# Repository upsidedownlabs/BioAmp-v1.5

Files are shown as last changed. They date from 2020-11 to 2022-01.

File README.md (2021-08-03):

# BioAmp v1.5

                       

BioAmp v1.5 is a single chip Bio-potential amplifier for recording any Bio-potential signal non-invasively. It's compatible with [Backyard Brains Spike Recorder](https://backyardbrains.com/products/spikerecorder), which you can use to record and visualize all the Bio-potential signals. 

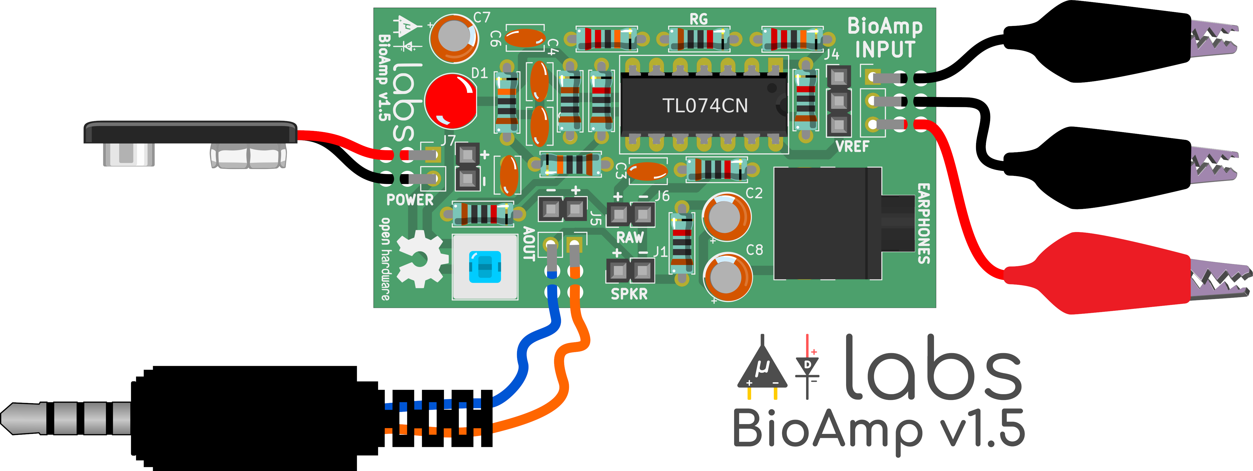
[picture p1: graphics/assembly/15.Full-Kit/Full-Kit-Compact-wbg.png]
Upside Down Labs BioAmp v1.5.6 back (https://bit.ly/BioAmp-v1_5)


## Hardware

BioAmp v1.5 has been created using [KiCad](https://www.kicad.org/) and all the design files can be found under [hardware](hardware/) folder, including production [Gerber](hardware/gerbers) files. Images below shows a quick overview of the hardware design.

| Front             |  Back |
| :-------------------------: | :-------------------------: |
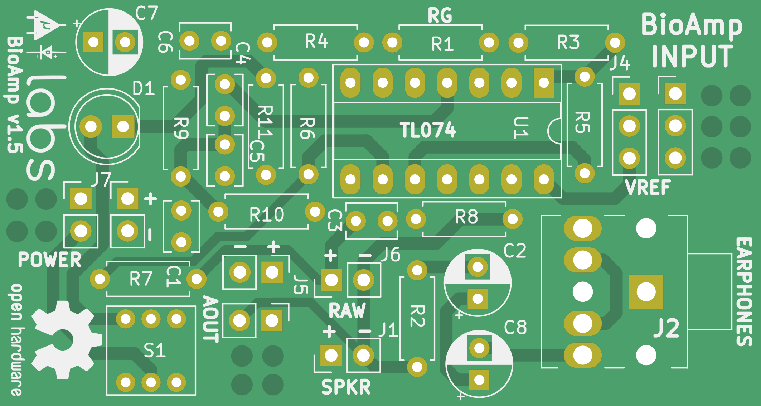
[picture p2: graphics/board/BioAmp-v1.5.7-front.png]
Upside Down Labs BioAmp v1.5.6 front
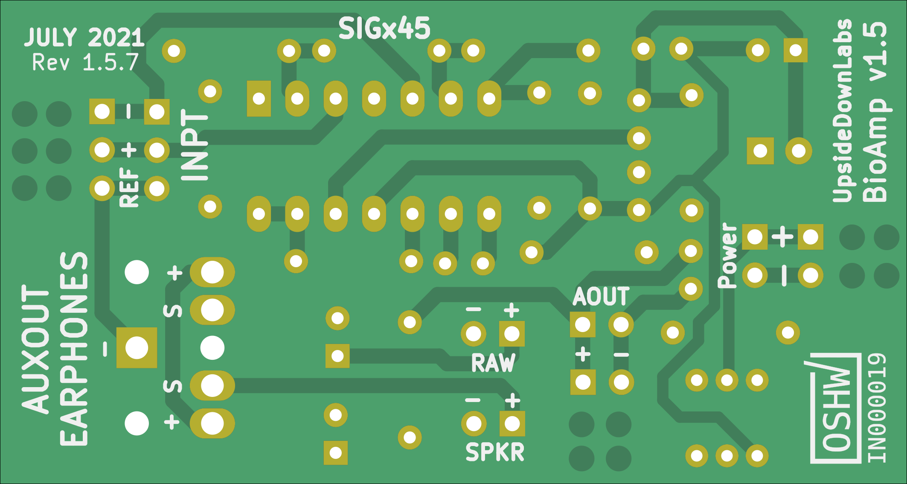
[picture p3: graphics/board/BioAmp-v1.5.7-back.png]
Upside Down Labs BioAmp v1.5.6 back
|   |  |

|Assembled PCB|
|:--:|
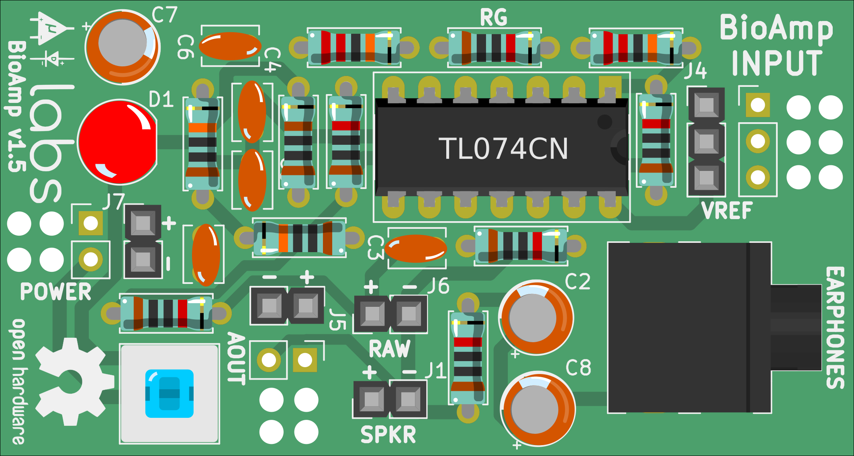
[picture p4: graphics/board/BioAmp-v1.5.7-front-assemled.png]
Upside Down Labs BioAmp v1.5.6 front
||

| Dimensions             |  Schematic  |
| :-------------------------: | :-------------------------: |
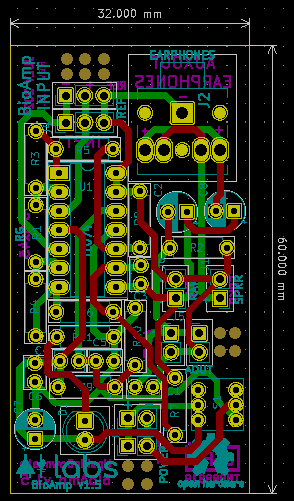
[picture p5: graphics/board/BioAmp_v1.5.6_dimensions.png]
Upside Down Labs BioAmp v1.5.6 dimensions
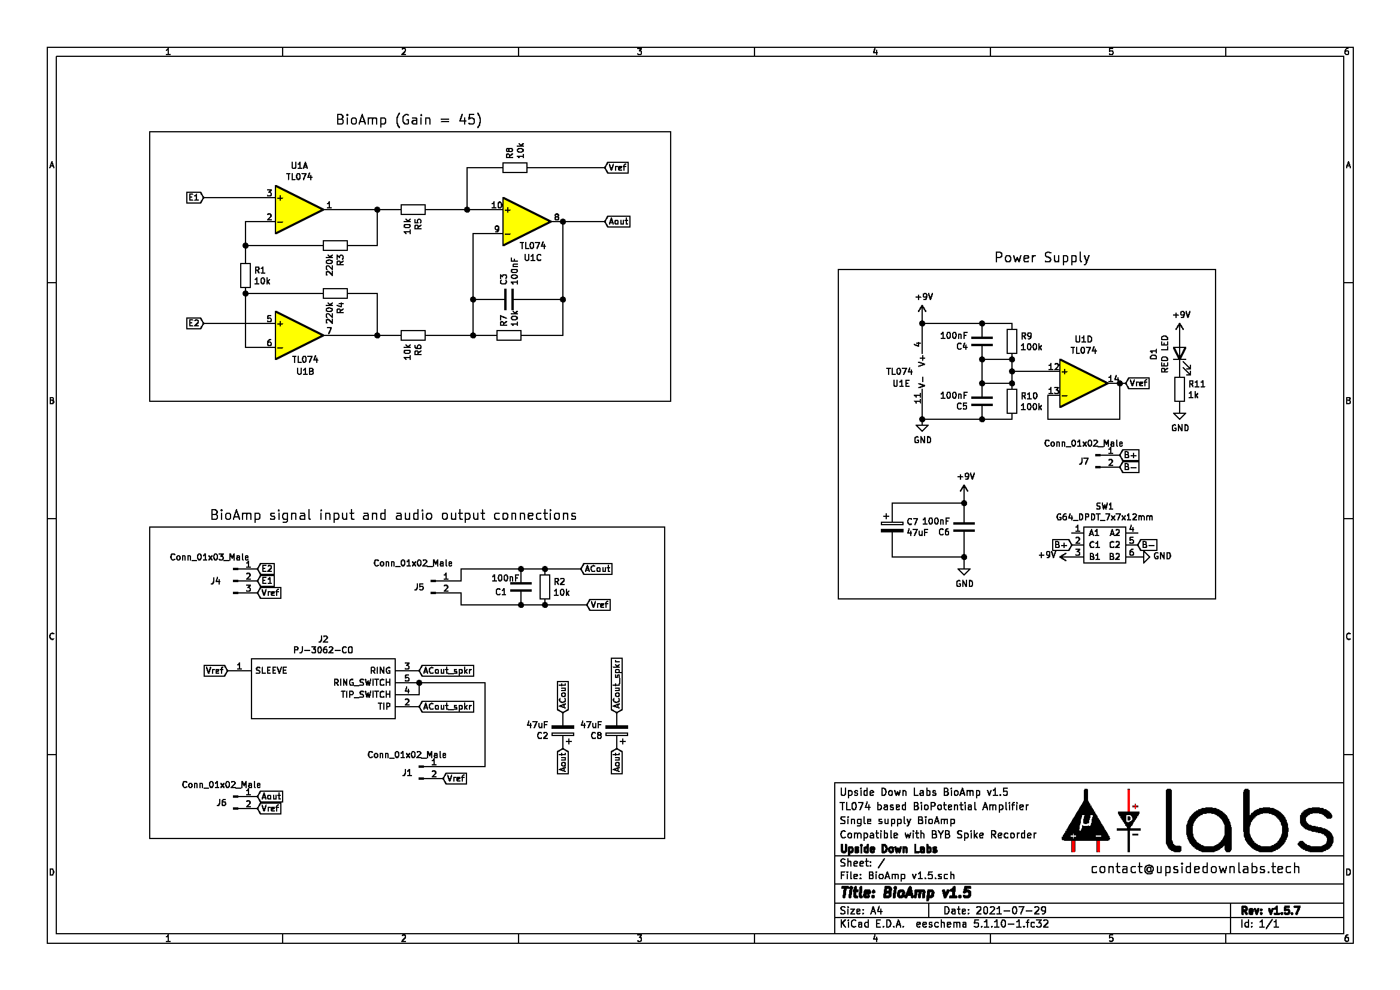
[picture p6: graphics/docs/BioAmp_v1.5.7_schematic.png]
Upside Down Labs BioAmp v1.5.6 schematic
| 32x60mm  |  |

| Licenses Facts              |  OSHWA Certification |
| :-------------------------: | :-------------------------: |
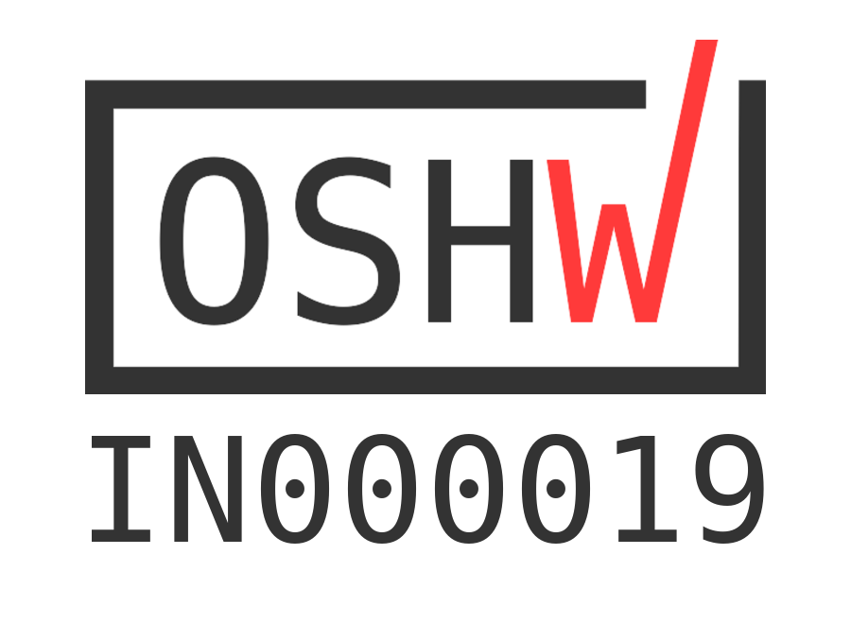
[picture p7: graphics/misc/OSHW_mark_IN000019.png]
Open Source Hardware Certification mark
| <a href="LICENSE.md">Open Source Licenses Facts</a>  |  |

## License
#### Hardware
CERN Open Hardware License Version 2 - Strongly Reciprocal ([CERN-OHL-S-2.0](https://spdx.org/licenses/CERN-OHL-S-2.0.html)).

#### Software
MIT open source [license](http://opensource.org/licenses/MIT).

#### Documentation:
<br />This work is licensed under a <a rel="license" href="http://creativecommons.org/licenses/by/4.0/">Creative Commons Attribution 4.0 International License</a>.

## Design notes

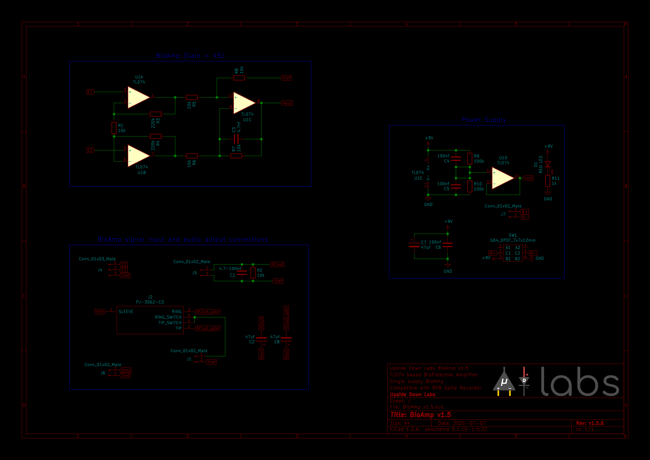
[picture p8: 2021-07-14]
graphics/docs/BioAmp_v1.5.6_schematic_hc.png

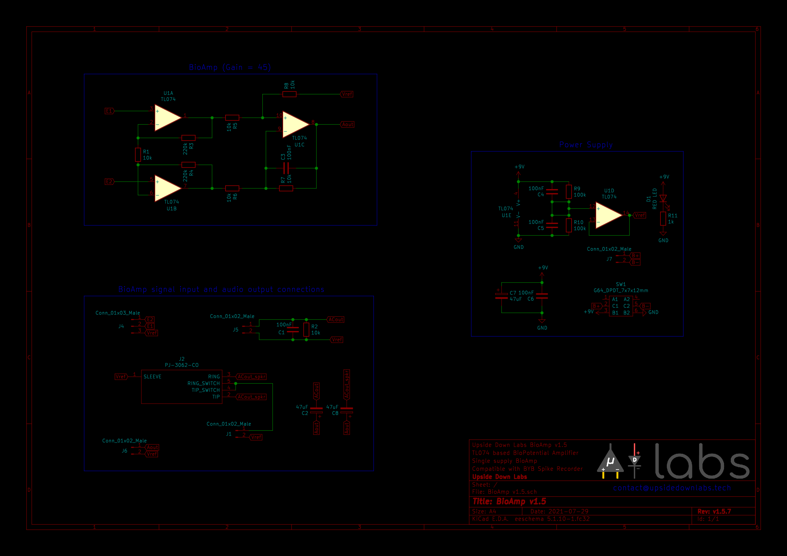
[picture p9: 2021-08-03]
graphics/docs/BioAmp_v1.5.7_schematic_hc.png

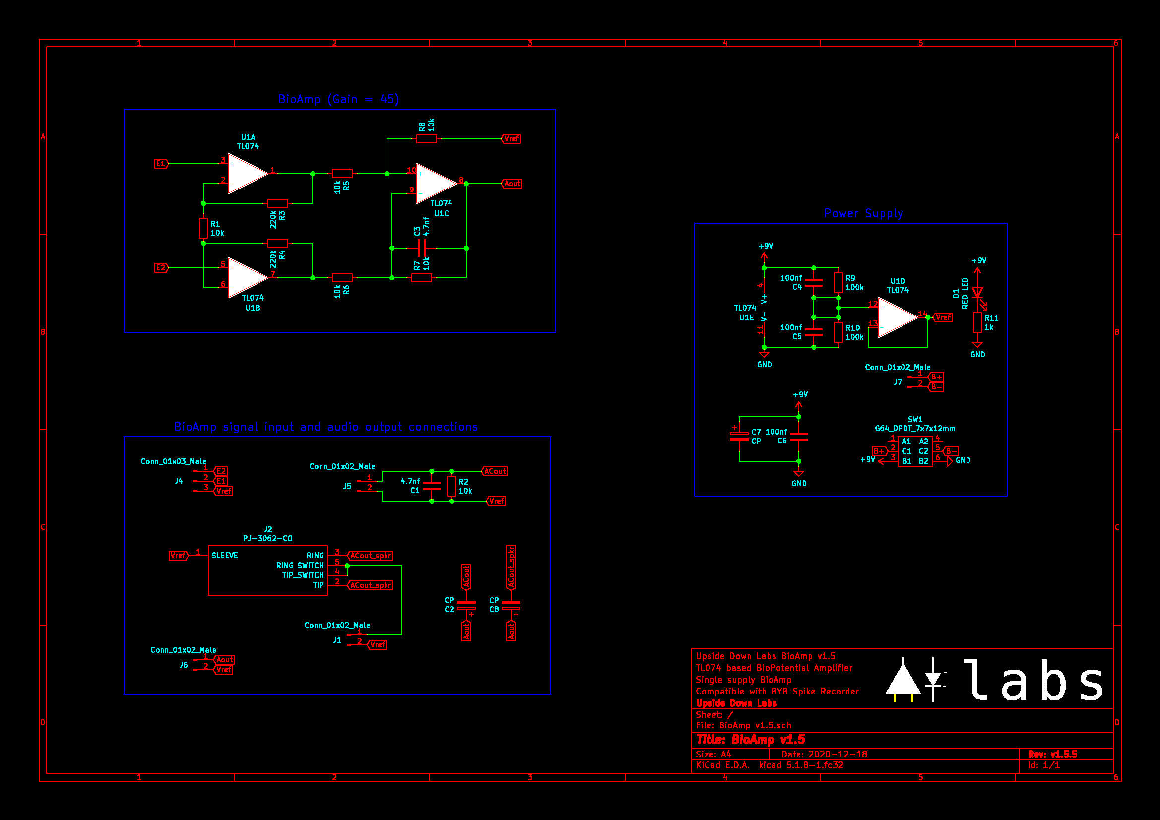
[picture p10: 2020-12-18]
graphics/docs/BioAmp_v1.5.5_schematic_hc.png

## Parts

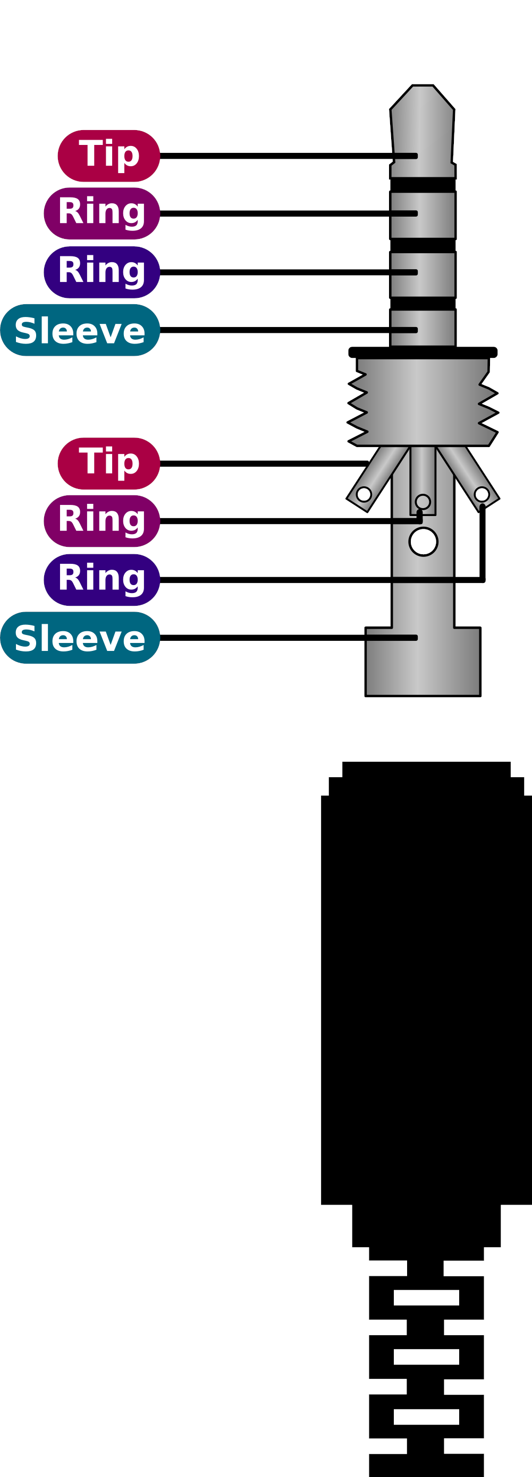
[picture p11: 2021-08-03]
graphics/assembly/Parts/3.5mm-Male/3.5mm-Male-wbg.png

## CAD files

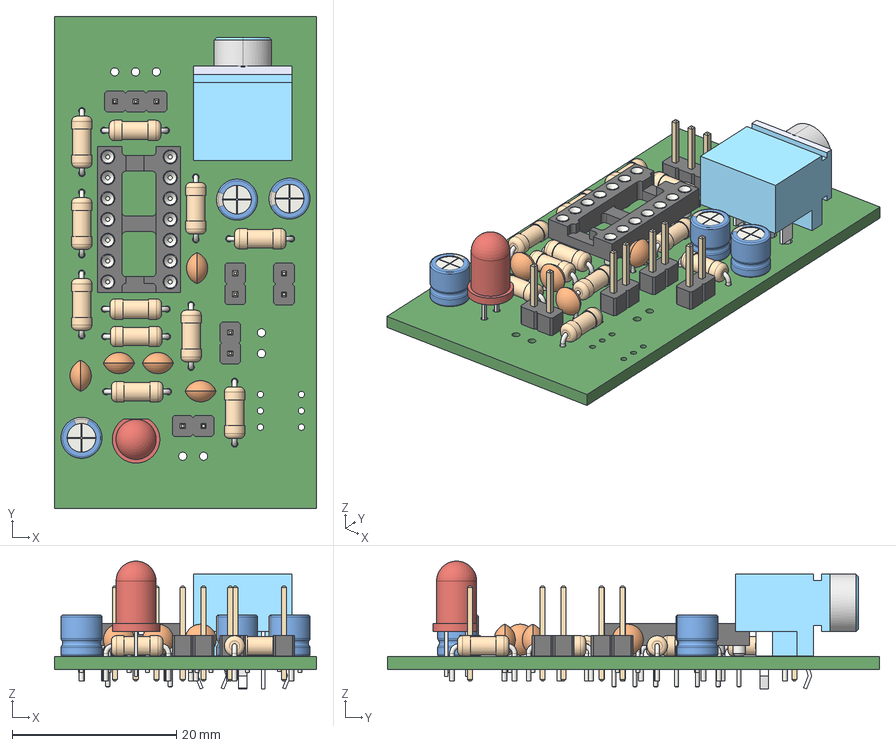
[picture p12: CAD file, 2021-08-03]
graphics/3D/BioAmp v1.5.step
32.0 x 60.0 x 15.6 mm

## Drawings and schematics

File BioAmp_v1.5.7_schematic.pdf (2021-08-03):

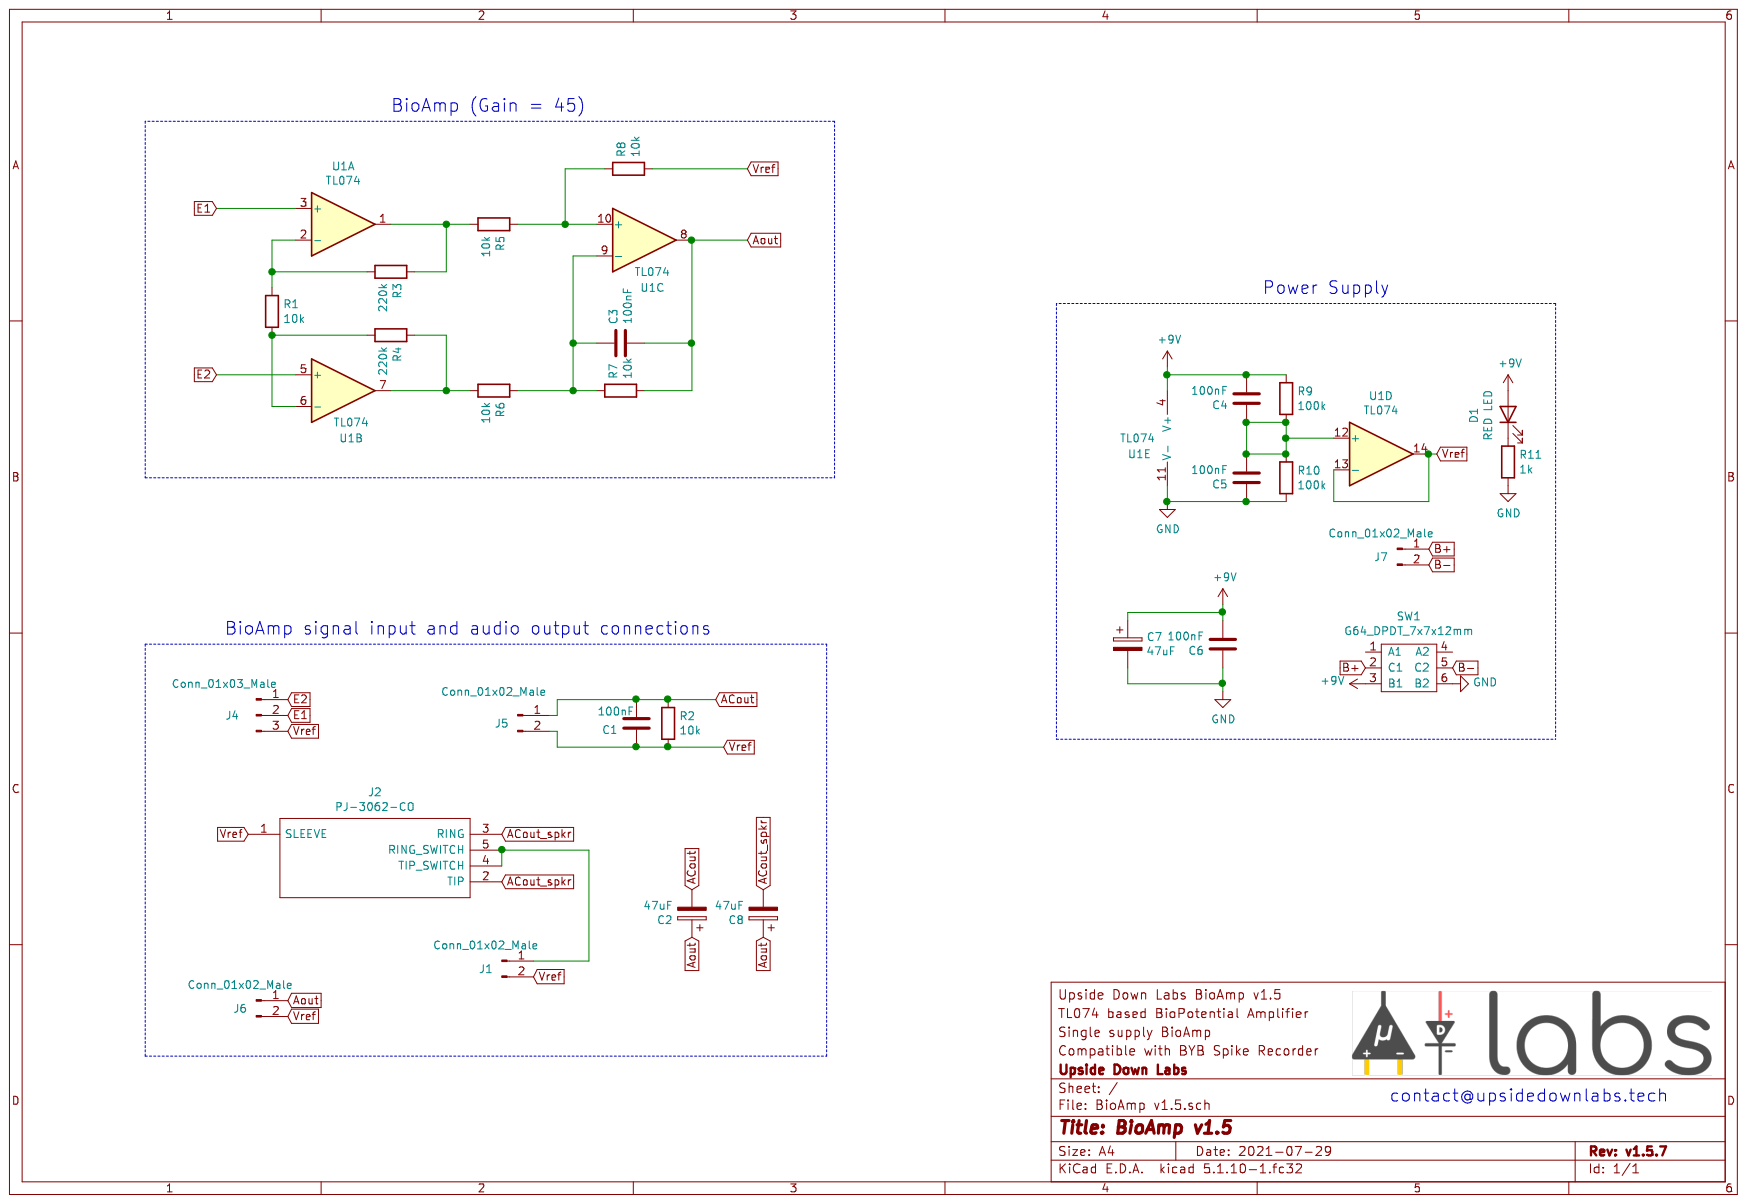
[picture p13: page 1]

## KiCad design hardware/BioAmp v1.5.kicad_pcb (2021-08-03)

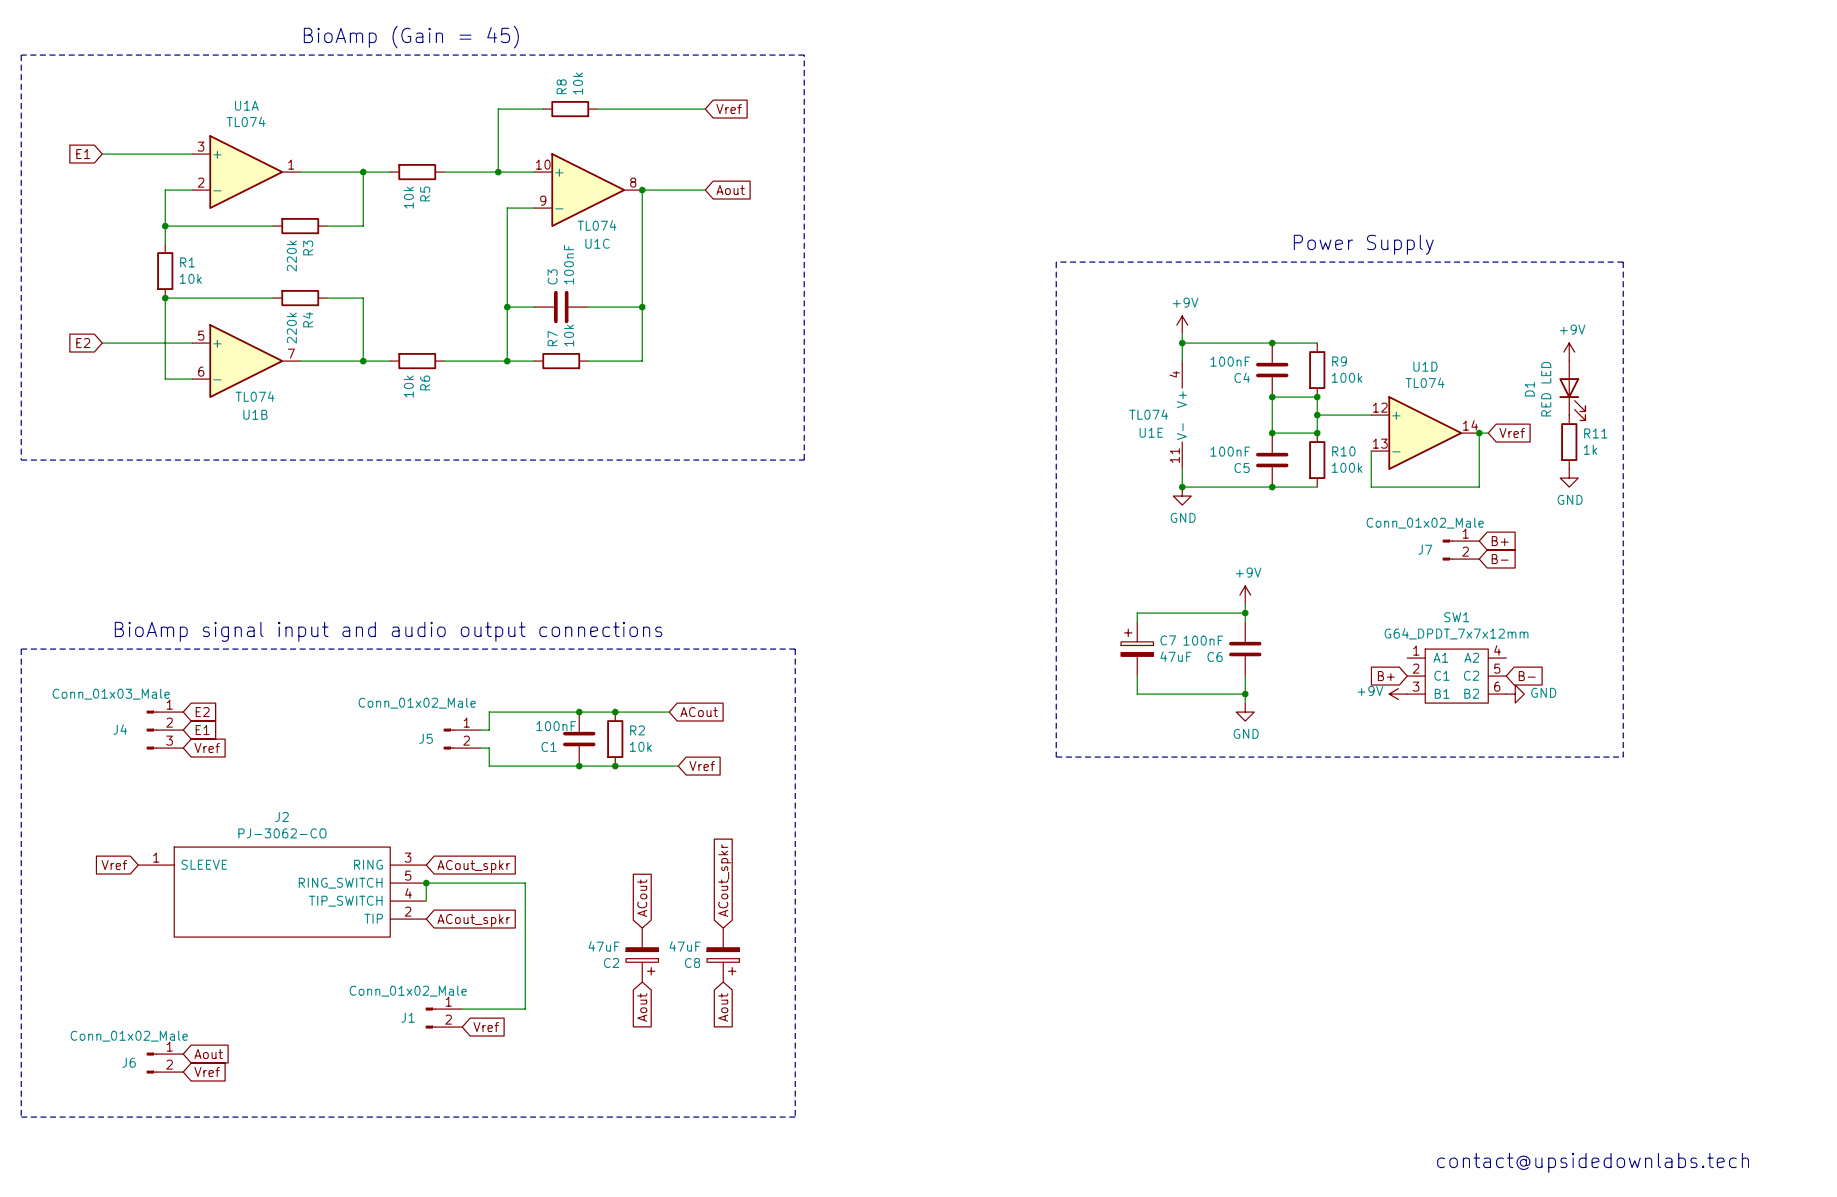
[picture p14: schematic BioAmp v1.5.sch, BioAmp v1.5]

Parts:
C1, C3, C4, C5, C6: 100nF; C_Disc_D3.8mm_W2.6mm_P2.50mm
C2, C7, C8: 47uF; CP_Radial_D5.0mm_P2.50mm
D1: RED LED; LED_D5.0mm
J1, J5, J6, J7: Conn_01x02_Male; PinHeader_1x02_P2.54mm_Vertical
J2: PJ-3062-CO; PJ3062CO; Manufacturer_Part_Number PJ-3062-CO
J4: Conn_01x03_Male; PinHeader_1x03_P2.54mm_Vertical
R1, R2, R5, R6, R7, R8: 10k; R_Axial_DIN0207_L6.3mm_D2.5mm_P7.62mm_Horizontal
R3, R4: 220k; R_Axial_DIN0207_L6.3mm_D2.5mm_P7.62mm_Horizontal
R9, R10: 100k; R_Axial_DIN0207_L6.3mm_D2.5mm_P7.62mm_Horizontal
R11: 1k; R_Axial_DIN0207_L6.3mm_D2.5mm_P7.62mm_Horizontal
SW1: G64_DPDT_7x7x12mm
U1: TL074; DIP-14_W7.62mm_Socket_LongPads

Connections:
+9V: C4.2, C6.2, C7.1, D1.2 (A), R9.1, SW1.3 (B1), U1.4 (V+); also elsewhere on the board
ACout: C1.2, C2.2, J5.1, R2.1; also elsewhere on the board
ACout_spkr: C8.2, J2.2 (TIP), J2.3 (RING)
Aout: C2.1, C3.2, C8.1, J6.1, R7.2, U1.8
B+: J7.1, SW1.2 (C1); also elsewhere on the board
B-: J7.2, SW1.5 (C2); also elsewhere on the board
E1: J4.2, U1.3 (+); also elsewhere on the board
E2: J4.1, U1.5 (+); also elsewhere on the board
GND: C5.1, C6.1, C7.2, R10.2, R11.2, SW1.6 (B2), U1.11 (V-); also elsewhere on the board
unnamed: C3.1, R6.1, R7.1, U1.9 (-)
unnamed: C4.1, C5.2, R9.2, R10.1, U1.12 (+)
unnamed: D1.1 (K), R11.1
unnamed: J1.1, J2.4 (TIP_SWITCH), J2.5 (RING_SWITCH)
unnamed: R1.1, R3.2, U1.2 (-)
unnamed: R1.2, R4.2, U1.6 (-)
unnamed: R3.1, R5.2, U1.1
unnamed: R4.1, R6.2, U1.7
unnamed: R5.1, R8.1, U1.10 (+)
Vref: C1.1, J1.2, J2.1 (SLEEVE), J4.3, J5.2, J6.2, R2.2, R8.2, U1.13 (-), U1.14; also elsewhere on the board

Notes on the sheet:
BioAmp (Gain = 45)
Power Supply
BioAmp signal input and audio output connections
contact@upsidedownlabs.tech

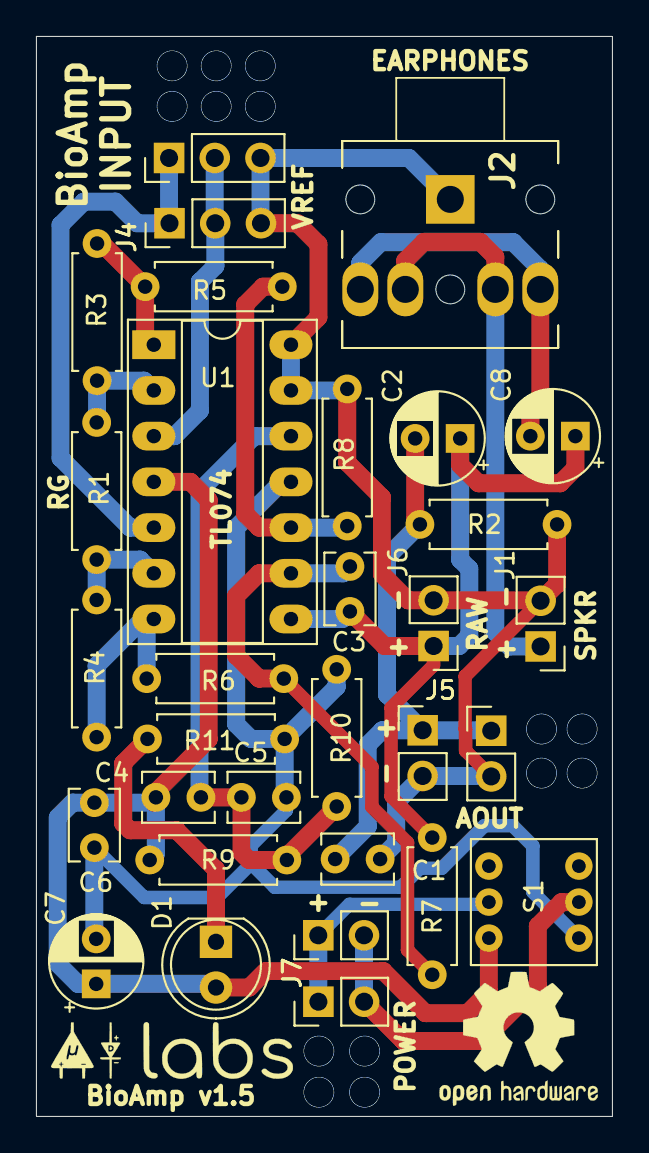
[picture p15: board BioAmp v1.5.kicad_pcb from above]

Board: 2 copper layers, 32.0 x 60.0 mm, 31 parts (0 on the bottom side), 19 nets.

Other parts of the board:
J4#2: Electode cable; PinHeader_1x03_P2.54mm_Vertical
J5#2: Audio cable; PinHeader_1x02_P2.54mm_Vertical
J7#2: Conn_01x02_Male; PinHeader_1x02_P2.54mm_Vertical
S1: TL2285EE; G64_DPDT

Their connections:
+9V: S1.3; also elsewhere on the board
ACout: J5#2.1; also elsewhere on the board
B+: J7#2.1, S1.2; also elsewhere on the board
B-: J7#2.2, S1.5; also elsewhere on the board
E1: J4#2.2; also elsewhere on the board
E2: J4#2.1; also elsewhere on the board
GND: S1.6; also elsewhere on the board
Vref: J4#2.3, J5#2.2; also elsewhere on the board

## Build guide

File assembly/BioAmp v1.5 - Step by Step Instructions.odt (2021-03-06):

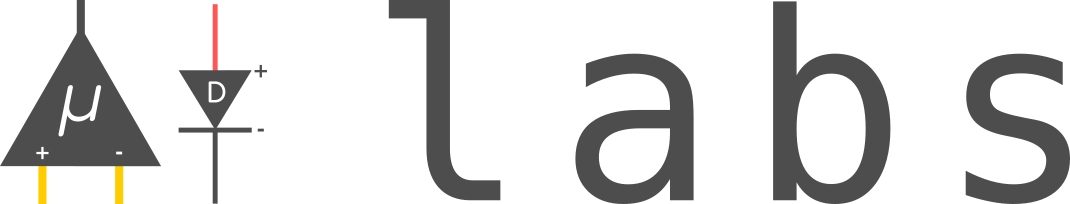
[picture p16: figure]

BioAmp v1.5 Instructions

March 2021

Materials Needed:

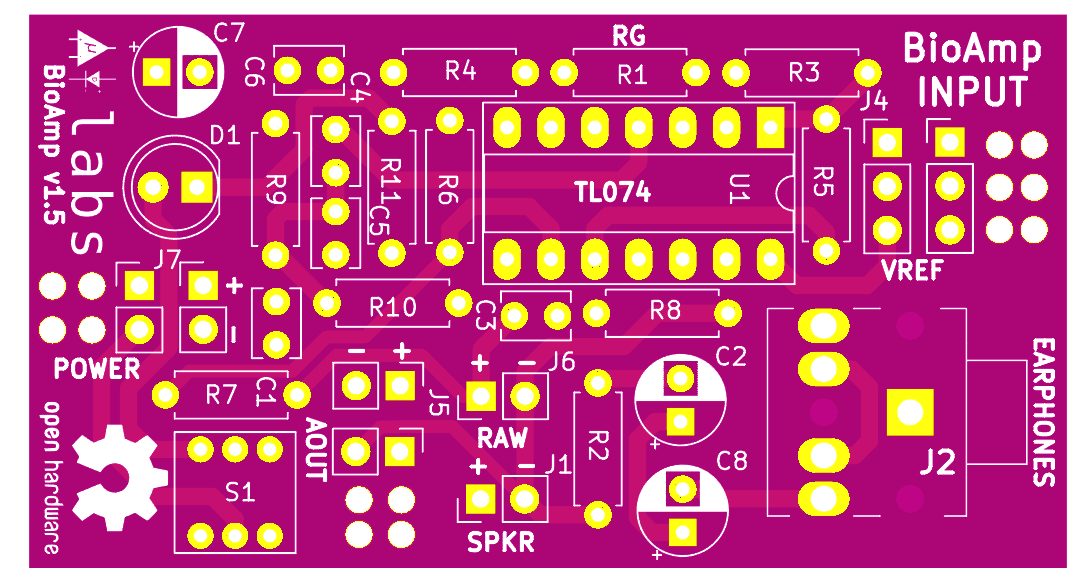
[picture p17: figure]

1. DIY BioAmp v1.5 Bag of Parts

2. Soldering Iron

3. Solder

4. Magnifying Glass to read labels on Capacitors

5. Silly Putty to hold components in place on board while you solder on the back of the board

6. Wire Strippers and Wire Clippers to trim leads

BioAmp v1.5 BOM:

Ref | Qnty | Value
C1, | 1 | 4.7-100nf
C2, C7, C8, | 3 | 47uf
C3, | 1 | 4.7nf
C4, C5, C6, | 3 | 100nf
D1, | 1 | RED LED
J1, J5, J6, J7, | 4 | Conn_01x02_Male
J2, | 1 | PJ-3062-CO
J4, | 1 | Conn_01x03_Male
R1, R2, R5, R6, R7, R8, | 6 | 10k
R3, R4, | 2 | 220k
R9, R10, | 2 | 100k
R11, | 1 | 1k
SW1, | 1 | DPDT_7x7x12mm
U1, | 1 | TL074
Alligator clips | 3 | Mini
3.5mm male | 1 | Jack with casing
BioAmp v1.5 PCB | 1 | PCB Board
Wires + Heat shrink | - | -

BioAmp v1.5 Circuit Construction:

Resistors

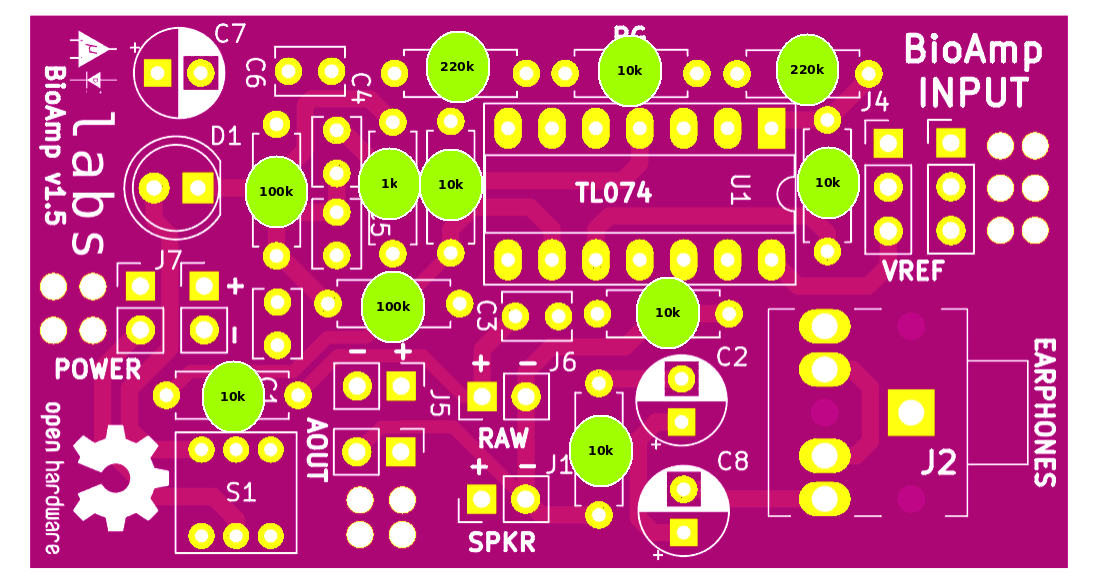
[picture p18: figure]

Capacitors

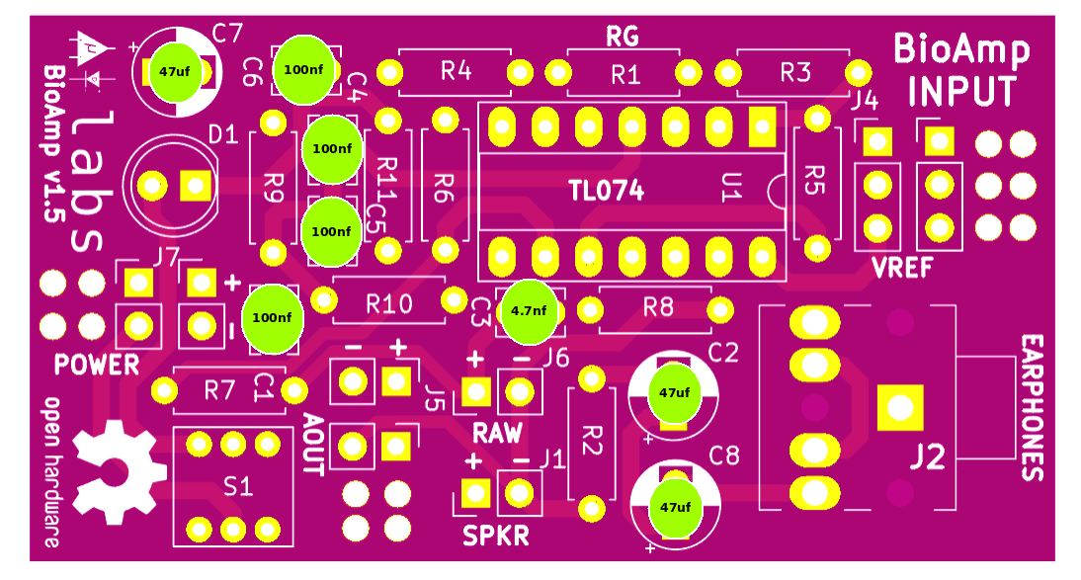
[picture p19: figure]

IC & LED

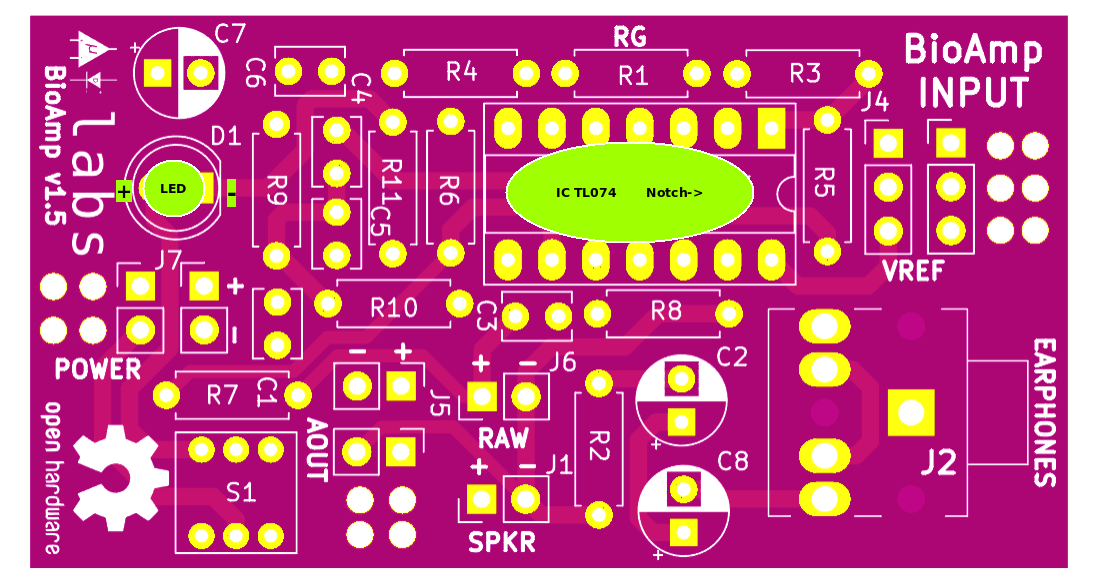
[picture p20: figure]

Connector & Switch

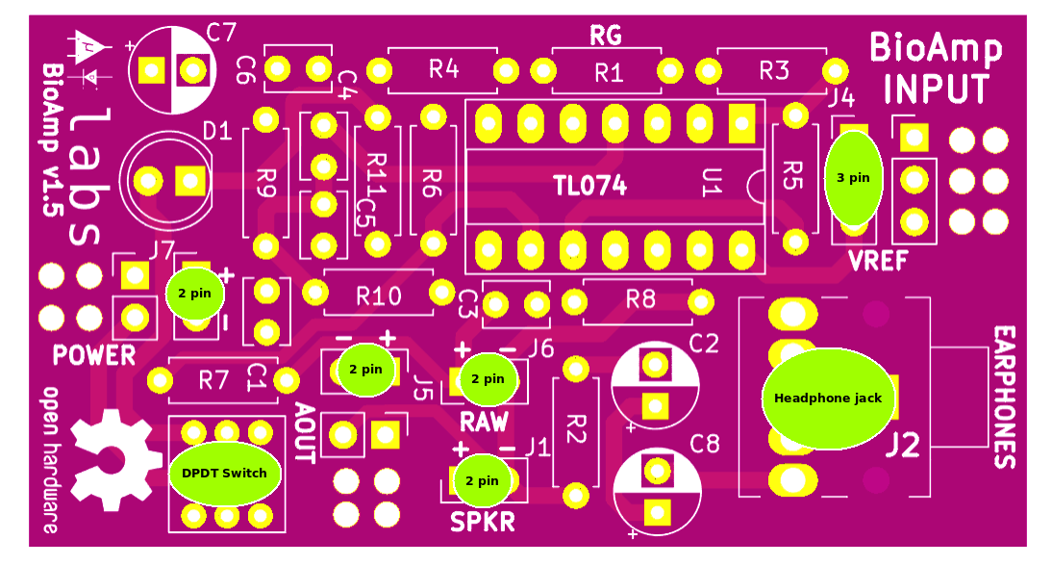
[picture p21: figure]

Cables

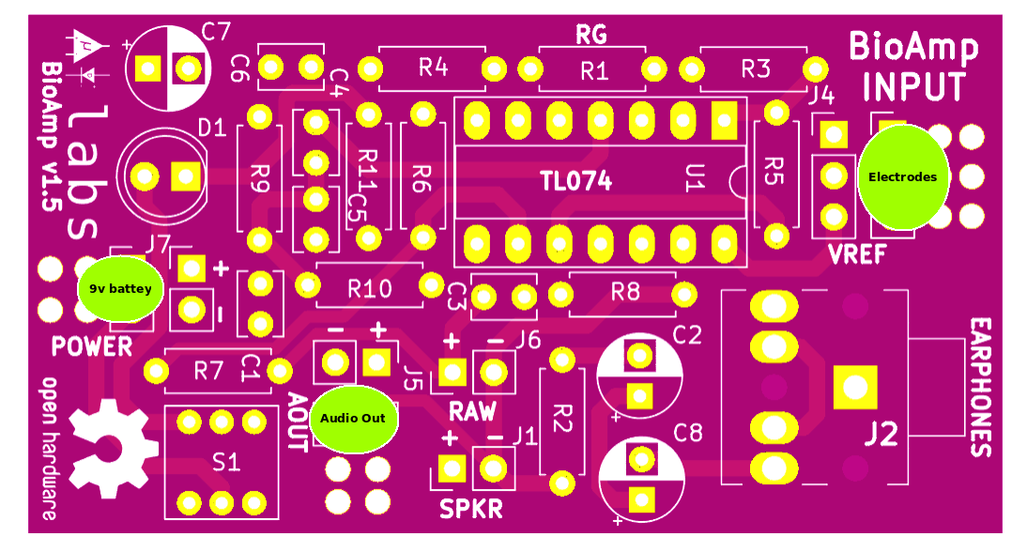
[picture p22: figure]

Fully Assembled BioAmp v1.5

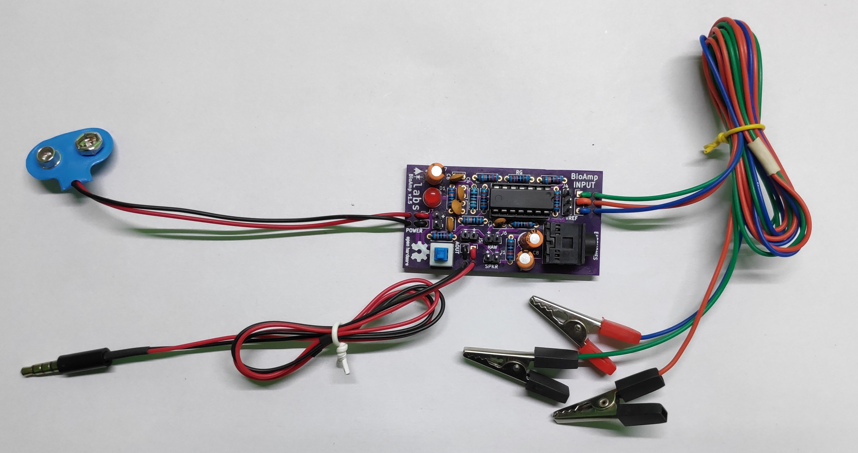
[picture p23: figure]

4 Upside Down Labs

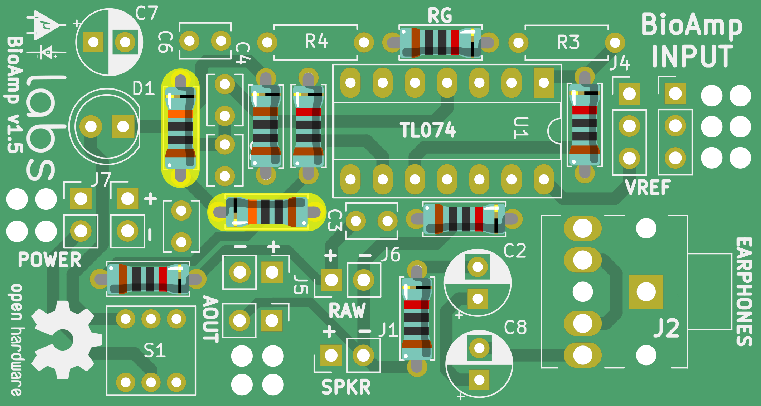
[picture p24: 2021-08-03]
graphics/assembly/03.Resistor-100k/Resistor-100k-wbg.png

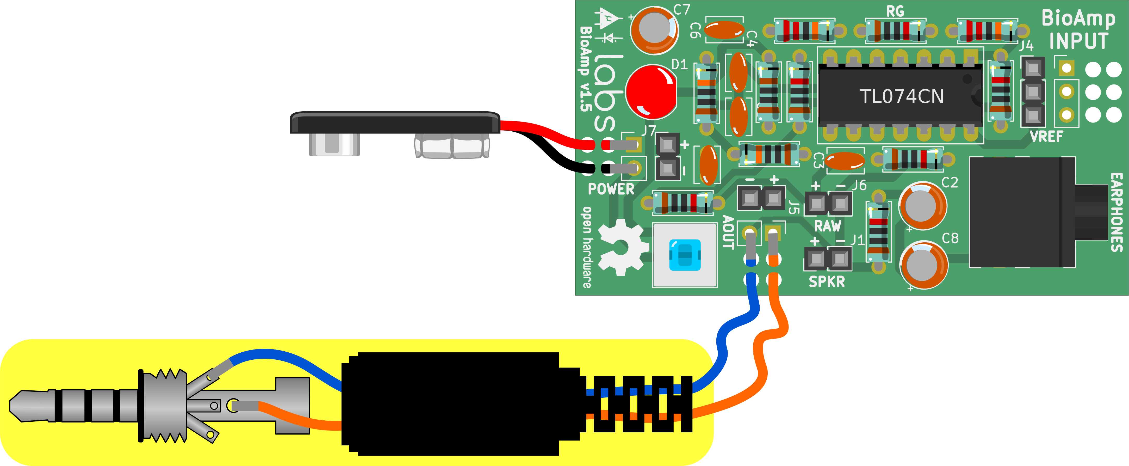
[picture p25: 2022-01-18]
graphics/assembly/13.Audio-Cable/Audio-Cable.png

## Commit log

2020-11-18 add 1.5.(1,2,3) boards
    [BioAmp v1.5.kicad_pcb, BioAmp v1.5.sch]
2020-11-18 fix Readme
    [BioAmp v1.5.kicad_pcb, BioAmp v1.5.sch]
2020-12-18 Old circuit not required
2020-12-18 Update to v1.5.5
    [BioAmp v1.5.kicad_pcb, BioAmp v1.5.sch]
2021-03-06 add assembly instructions manual
    This will help in the making of BioAmp v1.5 from the DIY kit we sell in Tindie.
2021-03-06 BioAmp v1.5 BOM for reference
    [BioAmp_v1.5_BOM.pdf.ods]
2021-03-06 Update schematic
    Updated the capacitor referneces
    [BioAmp v1.5.sch]
2021-03-06 BioAmp blank PCB image
    purple black PCB for reference purpose.
2021-03-06 Cable connection guide
2021-03-06 Capacitor assembly guide
2021-03-06 IC&LED assembly guide
2021-03-06 Connector&Switches assembly guide
2021-03-06 Resistor assembly guide
2021-03-06 BioAmp v1.5 fully assembled
2021-04-05 Cleanup & Rearrange files
    Initial cleanup for major software update. Awesome Python notebooks and scripts will be added soon :)
    [BioAmp_v1.5_BOM.ods]
2021-07-14 BioAmp v1.5.6 KiCAD PCB
    This version includes minor cosmetic changes,
    this will be the final revision of BioAmp v1.5!
    [BioAmp v1.5.kicad_pcb]
2021-07-14 BioAmp v1.5.6 KiCAD schematic
    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
    [BioAmp v1.5.sch]
2021-07-14 BioAmp v1.5.6 gerbers
    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
    [BioAmp v1.5-B_Cu.gbl, BioAmp v1.5-B_Mask.gbs, BioAmp v1.5-B_Paste.gbp, BioAmp v1.5-B_SilkS.gbo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]
2021-07-14 Re-arrange files
    changing directory structure to increase user accessebility.
    [BioAmp v1.5-B_Cu.gbl, BioAmp v1.5-B_Mask.gbs, BioAmp v1.5-B_Paste.gbp, BioAmp v1.5-B_SilkS.gbo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]
2021-07-14 BioAmp v1.5.6 KiCAD hardware files
    [BioAmp v1.5.kicad_pcb, BioAmp v1.5.sch]
2021-07-14 BioAmp v1.5.6 KiCAD gerber files
    [BioAmp v1.5-B_Cu.gbl, BioAmp v1.5-B_Mask.gbs, BioAmp v1.5-B_Paste.gbp, BioAmp v1.5-B_SilkS.gbo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]
2021-07-14 BioAmp v1.5.5 Dia diagram images (assembly)
2021-07-14 BioAmp v1.5.5 board images
2021-07-14 BioAmp v1.5.6 assembly instructions
2021-07-14 remove BOM folder
    [BioAmp_v1.5_BOM.ods]
2021-08-03 Updating...
    Removing unwanted files from the repo.
    [BioAmp v1.5-B_Cu.gbl, BioAmp v1.5-B_Mask.gbs, BioAmp v1.5-B_Paste.gbp, BioAmp v1.5-B_SilkS.gbo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]
2021-08-03 BioAmp v1.5.7 hardware files
    Small modification for the holes in this update.
    [BioAmp v1.5.kicad_pcb, BioAmp v1.5.sch]
2021-08-03 BioAmp v1.5.7 board images
    SVG and PNG of the final BioAmp v1.5.7 board
2021-08-03 9v battery snap
    SVG files for 9v battery snap.
2021-08-03 3.5mm male jack SVG and PNG
2021-08-03 15. Full kit
    BioAmp v1.5.7 fully assembled kit
2021-08-03 14. Electrode cable
2021-08-03 13. Audio cable
2021-08-03 12. Battery snap
2021-08-03 08. IC socket
2021-08-03 07. LED
2021-08-03 06. Capacitor 47uf
2021-08-03 05. Capacitor 100nF
2021-08-03 03. Resistor 100k
2021-08-03 Resistor 10k
2021-08-03 01. Resistor 1k
2021-08-03 00. Blank PCB
2021-08-03 BioAmp v1.5.7 3D STEP file
    [BioAmp v1.5.step]
2021-08-03 BioAmp v1.5 assembly guide
2021-08-03 Fully assembled BioAmp v1.5.7 PCB
2022-01-18 Update assembly instruction guide
    IC holder was shows incorrectly, it has been fixed now :)
